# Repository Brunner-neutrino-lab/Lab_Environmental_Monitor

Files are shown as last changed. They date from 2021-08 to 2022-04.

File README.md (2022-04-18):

# Project Description
The goal of this device is to be able to monitor air quality throughout the day with little maintenance, once the apparatus is fully set up. Everything depends on the Raspberry Pi, a microcontroller that can run programs and connect itself to various sensors. The sensors will measure the temperature, humidity, pressure, and dust levels. The Pi will take readings periodically, which will then be stored locally in the `Environmental_Data.csv` file. The key files of the project are: 
- `config.py` --> It allows the user to modify parameters such as reading and upload intervals, and sensor toggling .
- `Sensors_Functions.py` --> This file contains the functions needed to obtain readings from the sensors.
- `MAIN_PROGRAM.py` --> This file will take periodic readings of the surrounding environment 

# Weather Station Device Setup Guide 

This guide is here to help you connect and set up the different sensors to the Raspberry Pi. Everything works with the default `Raspbian OS`. If one needs help installing it onto the microSD card, visit [**this site**](https://projects.raspberrypi.org/en/projects/raspberry-pi-setting-up/2). If one wants to update their version, visit [**this site**](https://www.raspberrypi.org/documentation/raspbian/updating.md).

Once the OS is set up, and a keyboard and mouse are plugged in, please wire up the sensors as illustrated in the [**diagram**](https://github.com/Brunner-neutrino-lab/Lab_Environmental_Monitor/blob/main/DOCS/Photos/Wiring_Diagram.png). There are writen instructions [**here**](https://github.com/Brunner-neutrino-lab/Lab_Environmental_Monitor/blob/main/DOCS/WiringDiagram.md) if ever you need more details concerning the wiring.

If you are connecting an individual sensor without the use of `i2c`, you may skip over the next section, otherwise enabling the i2c interface is crucial for the sensor connection. The main program connects with all the sensors via the i2c interface. It allows for a more centralized and simple wiring scheme without using too many pins.

## Enabling the I2C interface

For a more detailed guide with photos, go [**here**](https://www.raspberrypi-spy.co.uk/2014/11/enabling-the-i2c-interface-on-the-raspberry-pi/).

Otherwise start by typing `sudo raspi-config` into the **Command line**

It will launch the raspi-config utility. From there:
- select **Interfacing Options** :
- Highlight the “I2C” option and activate: **Select**
- Select and activate: **Yes**
- If prompted to reboot highlight and activate: **Yes**

Once the i2c interface is set up and the devices are wired up, run the following command in the terminal: `sudo i2cdetect -y 1`. It will give you all the hexadecimal addresses for the devices which should be double-checked with the ones in the `config.py`. If the values do not match, modify them in the code so it matches the one from the terminal. You will only need to activate the i2c interface once and then you will not have to worry about it anymore.

## Software Setup

The first thing to do is to download the missing packages by entering the following commands in the terminal.

```
sudo apt install python3-pip
sudo apt install libatlas3-base
sudo pip3 install RPi.bme280
```

## How to run

Make sure everything is properly set up and that all the criteria below are met:
- i2c is enabled on the Raspberry Pi.
- The sensors are wired accordingly to the wiring [**diagram**](http://132.206.126.37/bvllab/particulate-sensor/blob/master/DOCS/Photos/Wiring_Diagram.png).
- The addresses from `i2cdetect -y 1` match the ones found in the `config.py` file.

Navigate through the directories until you are in the Main Folder. From there, run `nohup sudo python3 MAIN_PROGRAM.py &`. The nohup allows it to run even when the terminal is closed and the `&` symbol allows it to run as a background app. 

----------------

## Adding Additional Sensors

To add additional sensors, ideally they should be connected using the i2c module, making the wiring much easier and straight forward. The code to run the sensor should be in python, since most of the code is written in that language. 

- To start off, create a new variable in the `config.py` file to toggle the sensor on or off. It should be called something like NewSensor**Status** and will take values of either `1` or `0`. Then, in `Sensors_Functions.py` create the new variable: `NewSensor=config.NewSensorStatus`
- Once a systematic method of obtaining readings from the sensor is achieved, simply add a new function in the `Sensors_Functions.py` program before the `header()` function towards the end. The newly-created function should only return the observed reading such as temperature or pressure. No need for timestamps since the `Header()` function takes care of that. 
- In the `Header()` function, add a new "if" statement going along the lines of:
```
if NewSensorStatus==1:
    statement += ',NewSensor_units_used'
```
- Finally, in the `data()` function, add a new "if" statement looking like this:
```
if NewSensorStatus==1:
    statement += ',' + str(NewSensor())
```

## Contributors
- Felix Belair
- Chris Chambers
- Soud Al Kharusi

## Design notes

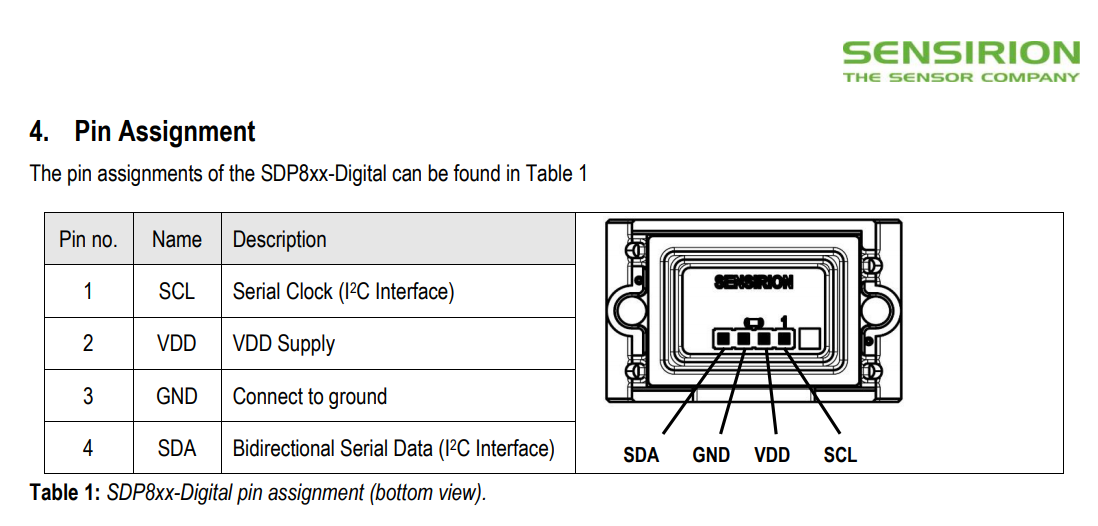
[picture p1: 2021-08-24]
DOCS/Photos/SDP810.png

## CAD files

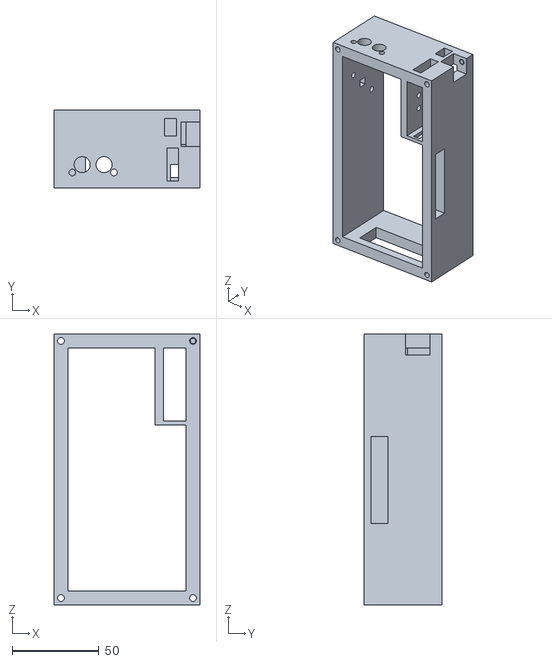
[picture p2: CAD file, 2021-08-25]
DOCS/3D Printing Files/LWS001_CaseBody.STL
84.0 x 45.0 x 156.0

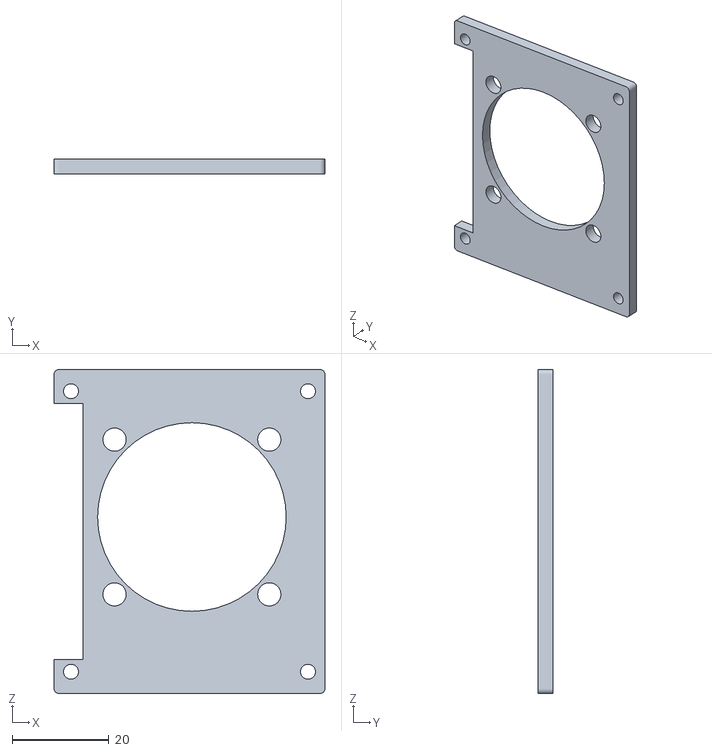
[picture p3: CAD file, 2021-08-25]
DOCS/3D Printing Files/LWS001_Fan_Bracket.STL
56.0 x 3.00 x 67.0

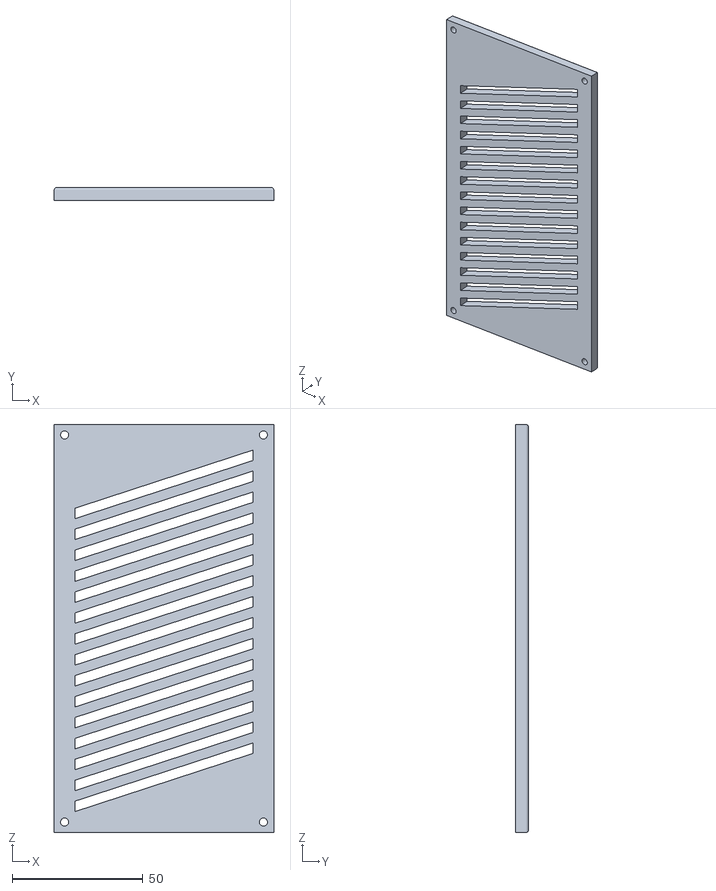
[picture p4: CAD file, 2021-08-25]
DOCS/3D Printing Files/LWS001_CaseLid.STL
84.0 x 5.00 x 156.0

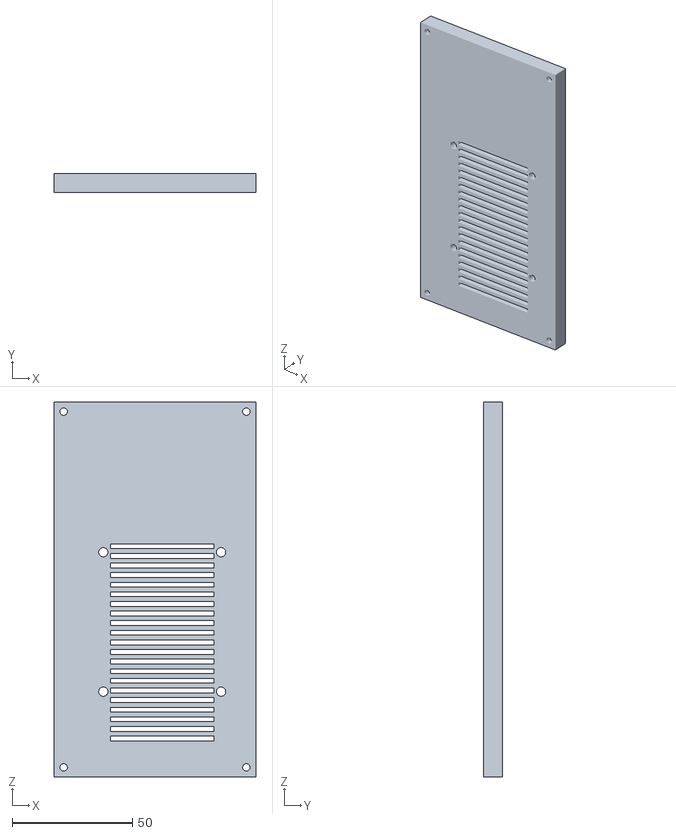
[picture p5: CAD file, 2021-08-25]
DOCS/3D Printing Files/LWS004_CaseBottom.STL
84.0 x 8.00 x 156.0

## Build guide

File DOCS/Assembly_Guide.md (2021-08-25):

# Brief Overview 

The goal of the project is to record environmental variables continuously over years with the use of various sensors such as a particulate counter or pressure differential sensor, to then upload the data to a server using a Raspberry Pi. Using various python submodules specific to each sensor, properties such as temperature, pressure differential, humidity, and dust levels are monitored and uploaded to a database at periodic time intervals. This would allow the user to verify whether the lab has a positive pressure differential relative to the outside to keep the dust out and to correlate when and how the dust particles enter. A 3d-printed case has been designed to package all these components together.

# Parts Needed 

* [Raspberry Pi 4](https://www.raspberrypi.org/products/raspberry-pi-4-model-b/) (The mastermind behind the project)
* [SPS30](https://www.sensirion.com/en/environmental-sensors/particulate-matter-sensors-pm25/) (Dust sensor)
* [SDP810](https://www.sensirion.com/en/flow-sensors/differential-pressure-sensors/sdp800-proven-and-improved/) (Pressure Differential sensor)
* [BME280](https://www.sparkfun.com/products/15440) (Atmospheric sensor that measures the Temperature, Humidity and Pressure)
* [Fan](https://www.sparkfun.com/products/15504) (will be placed above the Pi for it to cool off efficiently)
* [Small Soldering Board](http://www.proto-advantage.com/store/product_info.php?products_id=200062) (compact way to wire everything)
* 4x M2.5x6mm Standoffs (Raises the Pi slightly off the ground)--Must use this dimension since the openings for the Pi rely on the 6mm standoffs. McMaster-CARR number part:98952A103 
* 4x M2.5x12mm Standoffs (Raises the fan above the Pi)--Other heights may be used such as 14mm or 16mm if you do not have 12mm standoffs. McMaster-CARR number part:98952A109 
* 19x M2.5 Threaded Inserts (Allows us to use screws) McMaster-CARR number part:94180A321
* 10x M2.5x8mm Screws (used to attach fan onto the bracket, the lid, and SPS30) McMaster-CARR number part:91292A012
* 7x M2.5x10mm Screws (used to attach the BME280 and bottom part of the case) McMaster-CARR number part:91292A014
* 2x M2.5x16mm Screws (used to attach the SDP810) McMaster-CARR number part:91292A018
* 4x M4x16mm Screws (used for the fan) McMaster-CARR number part:90751A119
* 4x M4 nuts (also used for the fan) McMaster-CARR number part:91415A020
* Header pins (male and female)
* Jumper wires

# Software 
Here is a breif description of each program
* **The config.py** file can be modified by the user if ever they want to change something such as the time interval between scans or the I2C addresses for the sensors.
* **The MAIN_PROGRAM.py** does the data collection and the data upload.
* **The Sensors_Functions.py** is responsible for obtaining readings for all the sensors and for formatting the data. A python function is created for each sensor, and when called, returns a reading from that particular sensor. 

## Data File Format
The data being acquired is stored with headers....

* **timestamp:** This is the time at which the data was taken. The format is YYYY-MM-DD hh:mm:ss.
* **Temperature_C:** This is the temperature of the lab measured in Celsius. The readings should be around 21 degrees or so.
* **Pressure_Torr:** This is the pressure of the lab in Torr. Typically, the readings should be near 760Torr, which is the equivalent of 1 atmosphere.
* **Percent_Humidity:** This is the relative humidity in the air. At a given temperature, air can hold a certain amount of water vapor. Here it gives the ratio between the measured amount of water vapor present to the max carrying capacity at a given temperature.
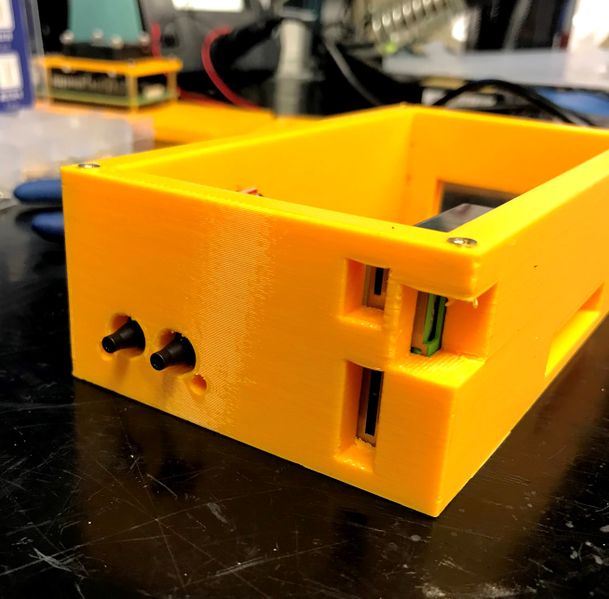
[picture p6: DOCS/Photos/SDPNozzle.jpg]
* **Differential_Pressure_Pa:** This is the difference in pressure between the 2 nobs on the SDP810, measured in Pascale. Once the SDP810 is placed inside the case, it will measure the pressure from the nozzle on right minus the pressure of the nozzle on the left, when viewed from this angle: 

It can give out both positive and negative values for the pressure difference, depending on which nozzle reads a higher pressure. This information comes from a diagram from this [data sheet](https://www.sensirion.com/fileadmin/user_upload/customers/sensirion/Dokumente/8_Differential_Pressure/Datasheets/Sensirion_Differential_Pressure_Datasheet_SDP8xx_Digital.pdf). 
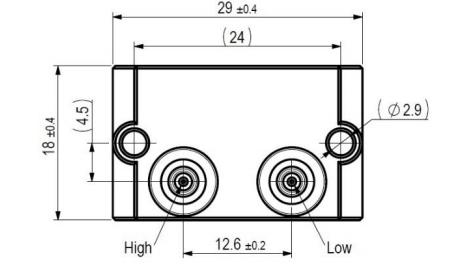
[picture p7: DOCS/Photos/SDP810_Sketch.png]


The sensor will return the difference between the High pressure nozzle to the Low pressure one in the diagram.

* **MC1um_ug_per_m3:** This measures the mass concentration of particles between 0.3um to 1um for a given volume of 1 meter cube in ug. In other words, take 1 meter cube of air and weigh all the particles between 0.3um and 1um and the total mass is the returned final reading (in ug). 
* **MC2point5um_ug_per_m3:** This measures the mass concentration of particles between 0.3um to 2.5um for a given volume of 1 meter cube in ug. In other words, take 1 meter cube of air and weigh all the particles between 0.3um and 2.5um and the total mass is the returned final reading (in ug). 
* **MC4um_ug_per_m3:** This measures the mass concentration of particles between 0.3um to 4um for a given volume of 1 meter cube in ug. In other words, take 1 meter cube of air and weigh all the particles between 0.3um and 4um and the total mass the final reading. 
* **MC10um_ug_per_m3:** This measures the mass concentration of particles between 0.3um to 10um for a given volume of 1 meter cube in ug. In other words, take 1 meter cube of air and weigh all the particles between 0.3um and 10um and the total mass is the returned final reading (in ug).
* **0point5um_Counts_Per_cm3:** This measures the number of particle counts between 0.3um to 0.5um for a given volume of 1 centimeter cube. In other words, take 1 centimeter cube of air and count all the particles between 0.3um and 0.5um and return the number of counts.
* **1um_Counts_Per_cm3:** This measures the number of particle counts between 0.3um to 1um for a given volume of 1 centimeter cube. In other words, take 1 centimeter cube of air and count all the particles between 0.3um and 1um and return the number of counts.
* **2point5um_Counts_Per_cm3:** This measures the number of particle counts between 0.3um to 2.5um for a given volume of 1 centimeter cube. In other words, take 1 centimeter cube of air and count all the particles between 0.3um and 2.5um and return the number of counts.
* **4um_Counts_Per_cm3:** This measures the number of particle counts between 0.3um to 4um for a given volume of 1 centimeter cube. In other words, take 1 centimeter cube of air and count all the particles between 0.3um and 4um and return the number of counts.
* **10um_Counts_Per_cm3:** This measures the number of particle counts between 0.3um to 10um for a given volume of 1 centimeter cube. In other words, take 1 centimeter cube of air and count all the particles between 0.3um and 10um and return the number of counts.
* **Typical_Particle_Size_um:** The typical particle size (TPS) gives an indication on the average particle diameter in the sample aerosol in um. Such output correlates with the weighted average of the number concentration bins measured with a TSI 3330 optical particle sizer. Consequently, lighter aerosols will have smaller TPS values than heavier aerosols.

# Physical Design 
Once all the components have been acquired (Raspberry Pi and sensors), a case has been designed to package everything together. The case is 3d printed and the **SolidWorks** design files can be found on [thingiverse](https://www.thingiverse.com/). At the moment, we are using the **Top_Fan_configuration** design, where the fan lies above the Raspberry Pi to cool it off. In that folder, the **3D print** folder contains all the parts that have to be printed (lid, main body, fan bracket, bottom case).

## Assembly Instructions (Top Fan Configuration)

To start, make sure you have all the material listed above and that the case components have been printed. 

### Fan and Bracket

* With the use of the **M4 nuts** and **M4x16mm screws**, clamp the fan onto the bracket. Ideally, the fan should be oriented such that the air should flow from below the bracket through the fan. This would ensure that the hot air is leaving the chip and going out of the case.
Here are 2 photos showing how it should look like once attached. 

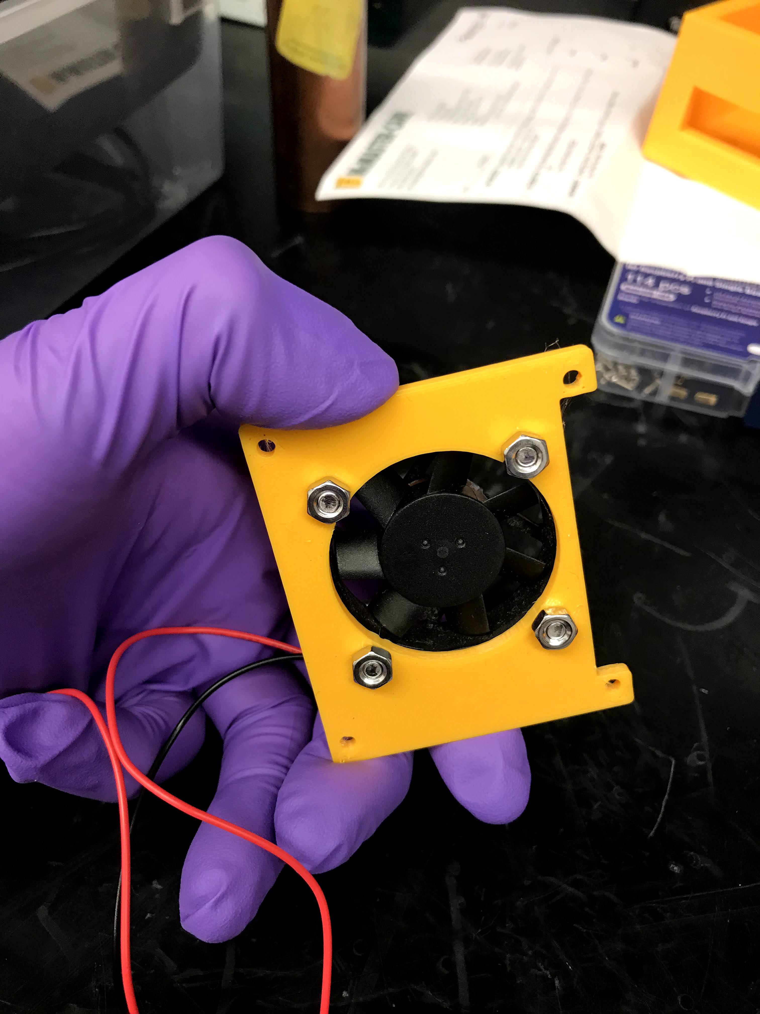
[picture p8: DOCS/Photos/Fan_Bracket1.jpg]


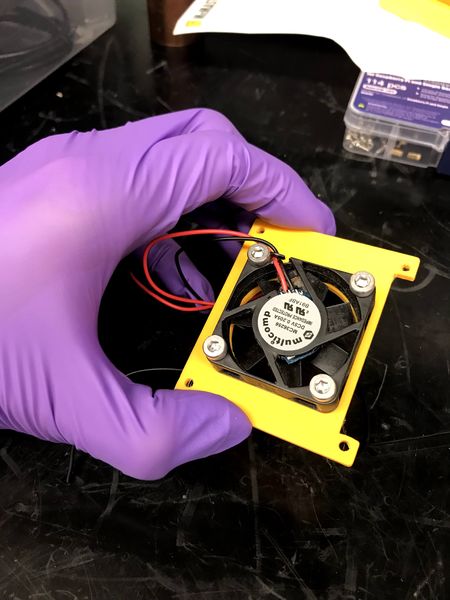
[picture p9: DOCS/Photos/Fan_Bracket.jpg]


Once this component is assembled, put it aside and we will use it in a few steps.

### Case Bottom

* Heat up and place the '''M2.5 threaded inserts''' into the 4 prearranged holes near the vent slits. They will be used to mount the Raspberry Pi.
* Once placed, screw in the '''M2.5x6mm Standoffs'''.

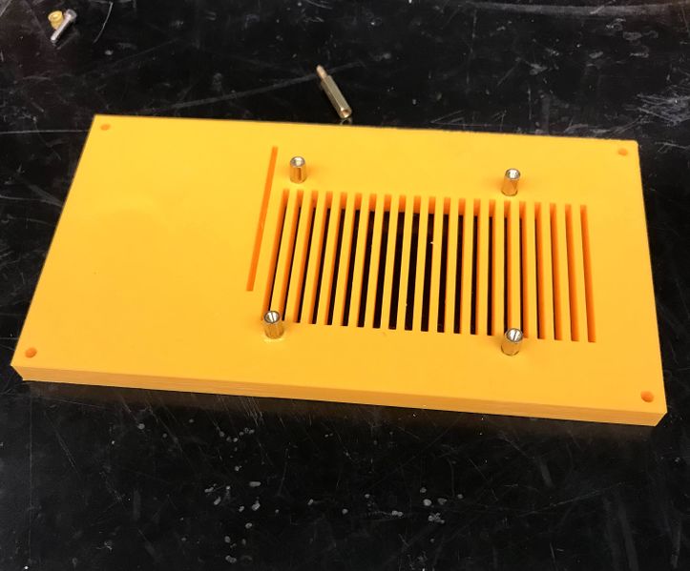
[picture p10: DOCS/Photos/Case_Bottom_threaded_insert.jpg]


* We can then proceed to mount the '''Raspberry Pi''' onto the corresponding standoffs by securing it with '''M2.5x12mm Standoffs'''. Make sure that the side with the USB and Ethernet ports is near the edge of the case and not the other way around. The 12mm standoffs will be used to place the fan above the Pi.

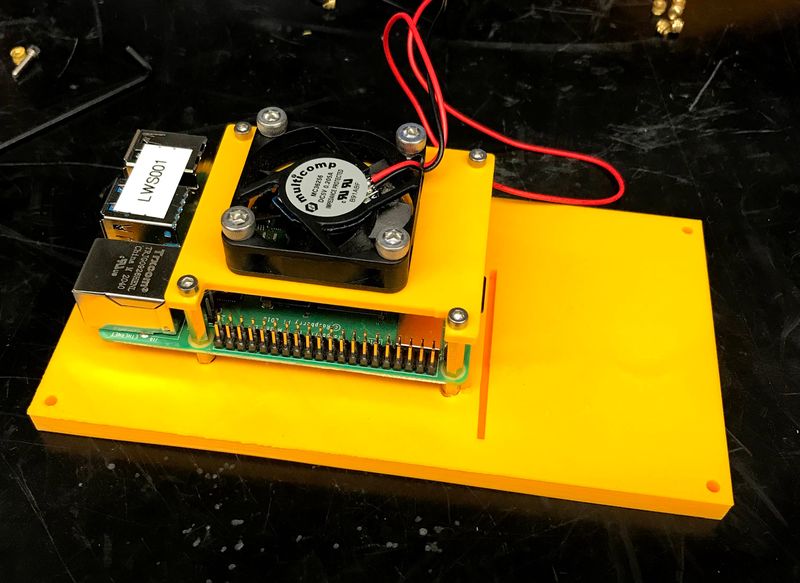
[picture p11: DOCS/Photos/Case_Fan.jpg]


* From there, we can take the Bracket-Fan component that we assembled in the first step, and mount it onto the standoffs using '''M2.5x8mm screws'''. For an optimal wiring experience, be sure to orient the bracket such that a hole is placed above the Raspberry Pi GPIO pins.

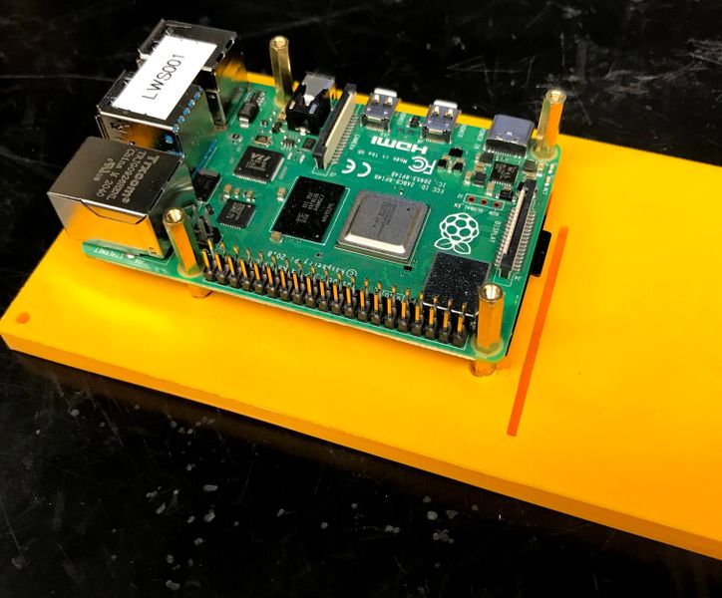
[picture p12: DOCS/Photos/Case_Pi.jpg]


### Main Body

* In the four outer corners of the main body of the case, heat up and place the '''M2.5 threaded inserts''' into the prearranged holes. Do this for the top and bottom holes of the corners.
* In all the inner holes of the case, heat up and place the '''M2.5 threaded inserts''' into the prearranged holes. This includes 2 for the SPS30, 3 for the BME280 and 2 for the SDP810.
* Place the '''SPS30''' in its assigned corner and fix it into place with 2 '''M2.5x8mm screws'''. Make sure the openings in the case align with the air intakes/outtakes of the sensor. 
* Place the '''SDP810''' by passing its 2 nozzles through the 2 wider holes. Make sure that it is oriented the right way up, such that its mounting holes align with the threaded inserts we placed earlier. Use 2 '''M2.5x16mm''' screws to secure it into place.
* The order of these steps is important since we cannot place the SDP810 once the BME280 is already placed. So once the SDP810 is mounted, we can now mount the '''BME280''' by inserting 3 '''M2.5x10mm screws'''. Make sure that the sensor component (the little box positioned in the middle) is facing outwards and aligned with the little opening.

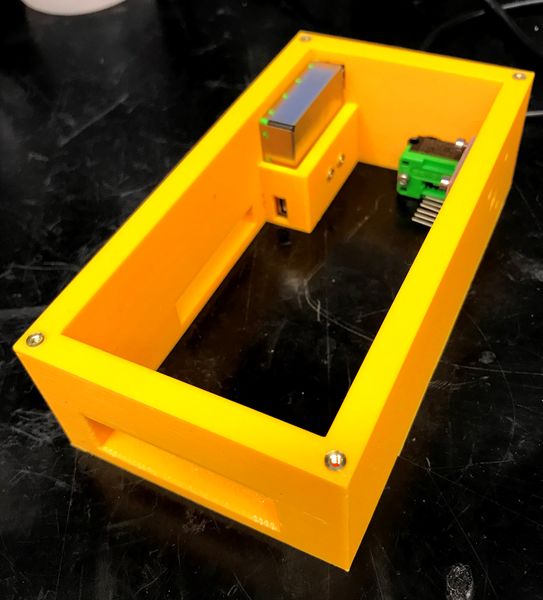
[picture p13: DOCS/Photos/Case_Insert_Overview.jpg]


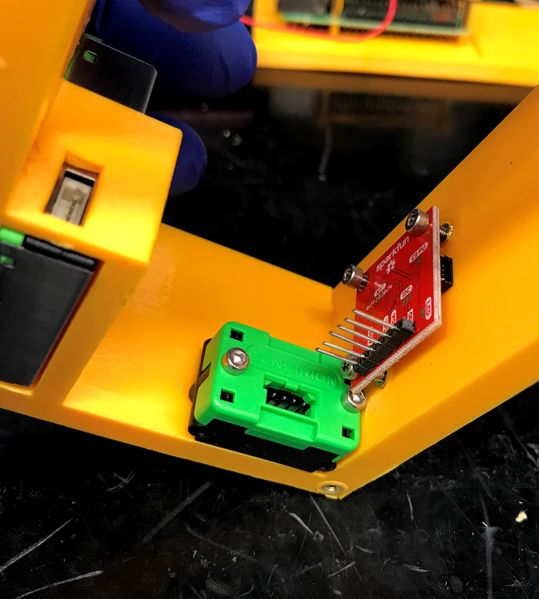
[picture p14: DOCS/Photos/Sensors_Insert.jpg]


### Soldering Board

* Using the small solder board, solder in a group of '''4 header pins''' for the RGB LED and a group of '''6 header pins''' for the rest of the sensors and the fan (the corresponding rows will be: 5V, 3.3V, SCL, SDA, Ground, Ground). The positioning is arbitrary, but in the photo, the header pins are placed in the upper row. These pins will be connected to the Pi with wires and the slots below them will connect to the various sensors. The use of the header pins allows us to rearrange a configuration without losing too much time. 

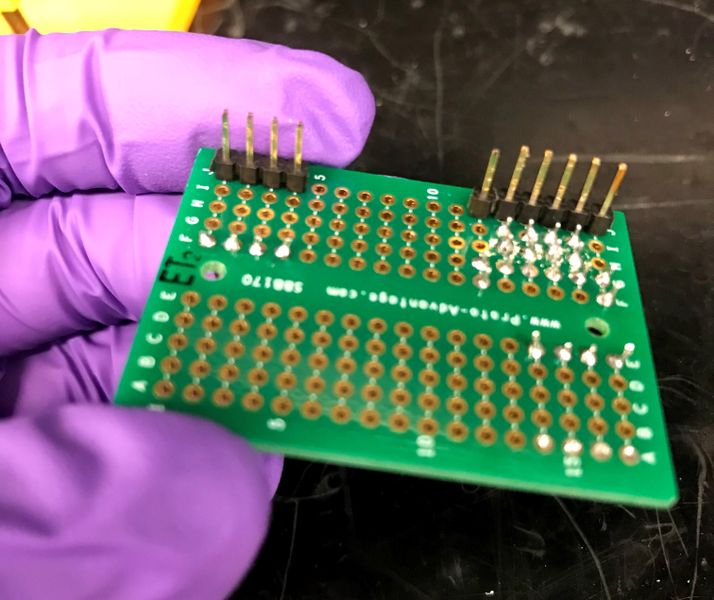
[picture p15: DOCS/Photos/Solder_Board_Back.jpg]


 In this photo, the 4 header pins for the RGB LED are placed on the far left, and the 6 others are placed on the right side of the board, all of which are on the top row.

* Flip the board over and solder in the '''RGB LED''' below the 4 header pins. Once the LED has been soldered, solder in '''female header pins''' in the same arrangement as the image below. 

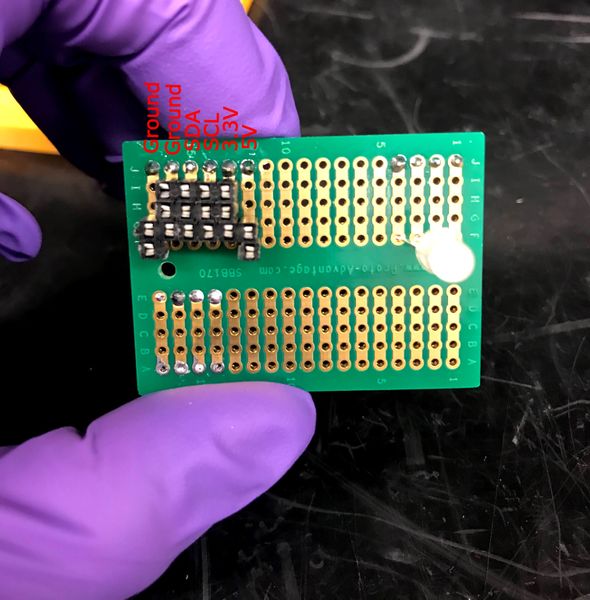
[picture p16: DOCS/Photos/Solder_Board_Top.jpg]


### Wiring

* After all the pins have been soldered, each sensor will connect their '''Ground, power source (3V or 5V), SDA, and SCL''' wires to their corresponding columns. The BME280 and SDP810 will use the first 2 rows (the order does not matter) since they both need the same 4 pins: 3V, SDA, SCL, and ground. The row with 6 pins is for the SPS30, as it will use everything except for the 3V pin (it is easier to solder in 6 consecutive pins, rather than having a hole in the middle). Finally, the fan will only use the 5V and the ground pin in the bottom row. If you take a closer look at the previous image (by clicking on it), you will see a column layout that has worked. From there, all the SDA pins will group up in the same column. The same is done for all the other pin types mentioned above (Ground, 3V, 5V, SDA, SCL). 

Wire layout for each sensors:
* If we look at the the '''SPS30''' (dust sensor) with the metal cap facing right and the wires pointing towards us, the top pin is #1 and the one in the bottom is #5. Then the pin roles are:
    * pin 1: 5V    (be careful to not connect it with the other 3.3V)
    * pin 2: SDA
    * pin 3: SCL
    * pin 4: Ground
    * pin 5: Ground (Very important to connect both grounds)

* If we look at the '''SDP810''' (pressure differential sensor) with the logo Sensirion facing upright. The pin on the very left will be pin 4 and the pin on the far right will be pin 1. 
    * Pin1 SCL
    * Pin2 3.3V
    * Pin3 Ground
    * Pin4 SDA

For the '''BME280''', the pins should be physically labeled, so no worries there. Do not worry if there are some unused pins on the BME280, since we only use 3V, Ground, SDA and SCL.

For the '''Raspberry Pi''', this photo should help out a bit.

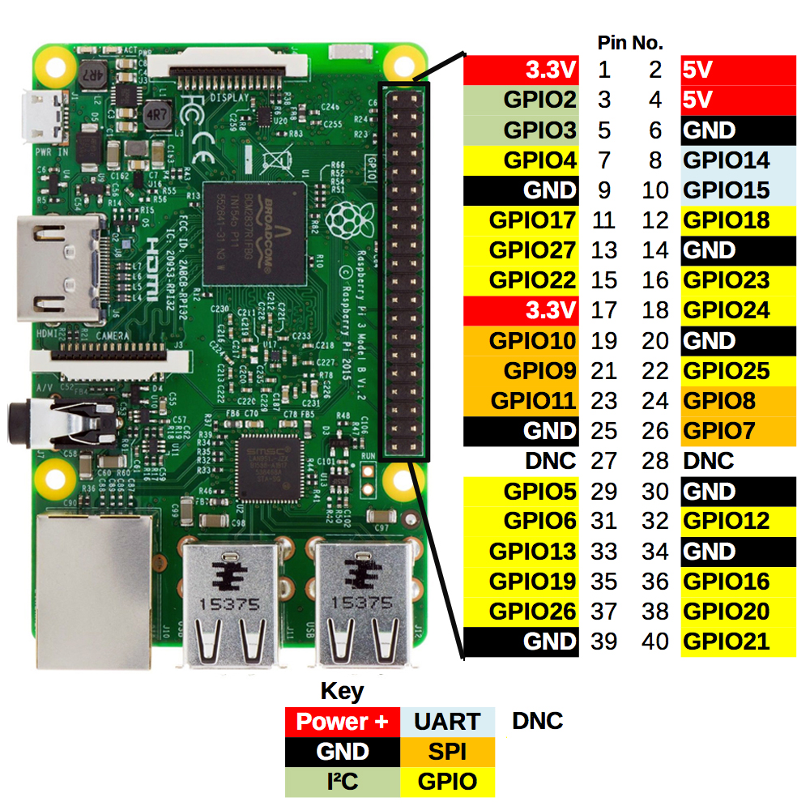
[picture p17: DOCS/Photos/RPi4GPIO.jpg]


*GPIO2 is for SDA and GPIO3 is for SCL.
*By default, the pins for the '''RGB LED''' are Red: GPIO13, Green: GPIO19, Blue: GPIO26. 

Here is a wiring diagram to help out. 



At first, it may look a little messy...

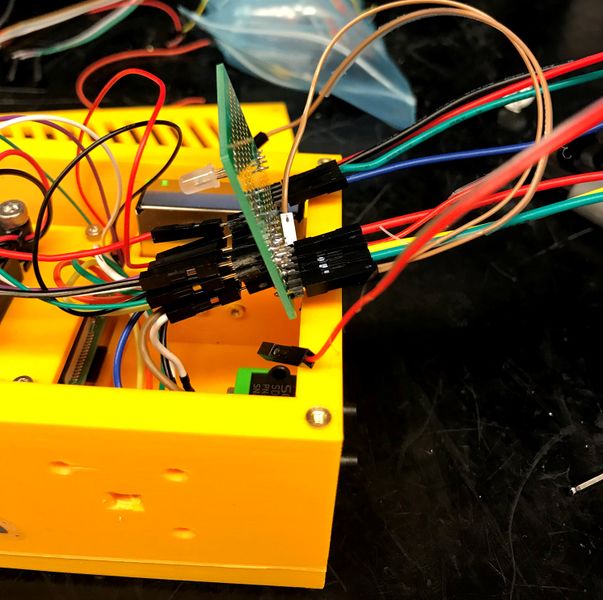
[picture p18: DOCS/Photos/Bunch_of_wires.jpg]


but once the Pi is wired up and we orient things a little better, things can place out to look like this:

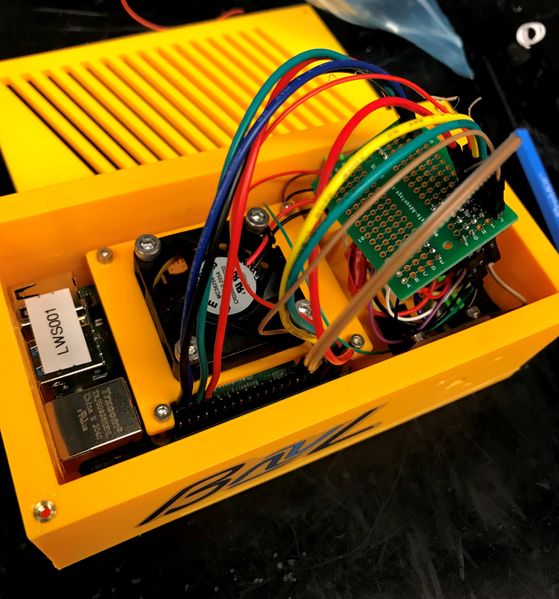
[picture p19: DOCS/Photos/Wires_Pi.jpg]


### Final Assembly

* Once things are wired up properly, flip the case over and mount the '''Case Bottom''' onto the Main Body with 4 '''M2.5x10mm''' screws. 
* Finally, flip the case over one last time to secure the '''Case Lid''' onto the Main Body with 4 '''M2.5x8mm''' screws.

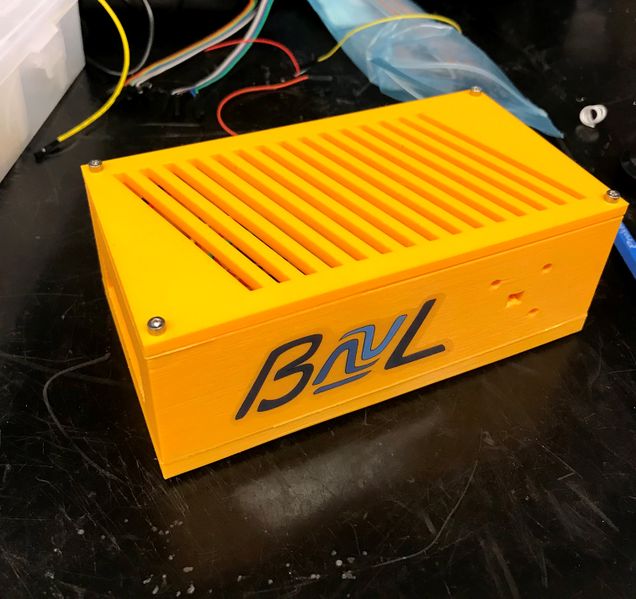
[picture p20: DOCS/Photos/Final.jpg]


# Known Issues

* If it is the first time running the program since it was last updated and errors are returned before it returns any readings, try rerunning the program once or twice.

* Another issue could be a wiring problem. Make sure all the components are wired properly. Take time to douche-check the wiring diagram to see if all the connections follow it. Make sure an electrical contact is properly made for all the sensors. It may be obvious if it is a jumper wire that is disconnected, but not so obvious if its the connector for the SPS30 or SDP810.

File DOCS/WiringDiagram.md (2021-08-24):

### Quick overview
For each sensor we will only need 4 connections: SDA, SCL, Voltage source, and ground. Even if there may be extra pins on the sensors, we will only need the 4 aforementioned pins. Since each sensor has a unique i2c address, all the SCL pins can be grouped up in the same column on a breadboard. The same should be done for the SDA pins. There are a few details concerning the power supply since the SPS30 uses 5V rather than 3.3V. Once all the wiring info is settled, you may wire up your sensors accoring to the [diagram](http://132.206.126.37/bvllab/particulate-sensor/blob/master/DOCS/Photos/Wiring_Diagram.png). To start off, we will first have to figure out which wires will do what.

### Pin labeling

For the **BME280**, the pins roles should be physically labeled on the sensor itself, so you shouldn't break a sweat for it. Soldering header pins is something I would recommend if it hasn't been done yet for that sensor. Do not worry if there are a few pins that will remain unused.

---------------------------------------------------------

If we look at the the **SPS30** (dust sensor) with the metal cap facing up, the pin on the left is pin 1 and the one on the right is pin 5. The pin roles are:

- pin 1: 5V    (be careful to not connect it with the other 3.3V)
- pin 2: SDA
- pin 3: SCL
- pin 4: Ground 
- pin 5: Ground (Very important to connect both grounds)

The reason why there are 2 ground wire connections, is because pin 4 determines how we connect the device. If it hangs there doing nothing, we select UART, and if we ground it, it chooses the i2c interface, which is what we are using. Furthermore, the ground pins cannot be connected with the ones from the other sensors since the voltage is different. For further guidance, here is a [diagram](http://132.206.126.37/bvllab/particulate-sensor/blob/master/DOCS/Photos/SPS30.png) of the sensor.

---------------------------------------------------------

If we look at the **SDP810** (pressure differential sensor) with the logo *Sensirion* facing upright. The pin on the very left will be **pin 4** and the pin on the far right will be **pin 1**. Please note that the order of the wires is different from the SPS30. For further guidance, here is a [diagram](http://132.206.126.37/bvllab/particulate-sensor/blob/master/DOCS/Photos/SDP810.png) of the sensor.

- Pin1 SCL
- Pin2 3.3V
- Pin3 Ground
- Pin4 SDA

---------------------------------------------------------
and finally for the Raspberry Pi we have:

- pin 1: 3.3V
- pin 2: 5V
- pin 3: GPIO2 ==>SDA
- pin 5: GPIO3 ==>SCL
- pin 6: GROUND (for the 5V dust sensor)
- pin 9: GROUND (for the 3.3V sensors)

This [diagram](http://132.206.126.37/bvllab/particulate-sensor/blob/master/DOCS/Photos/RPi4GPIO.jpg) shows the function of each pin on the Raspberry Pi 4.

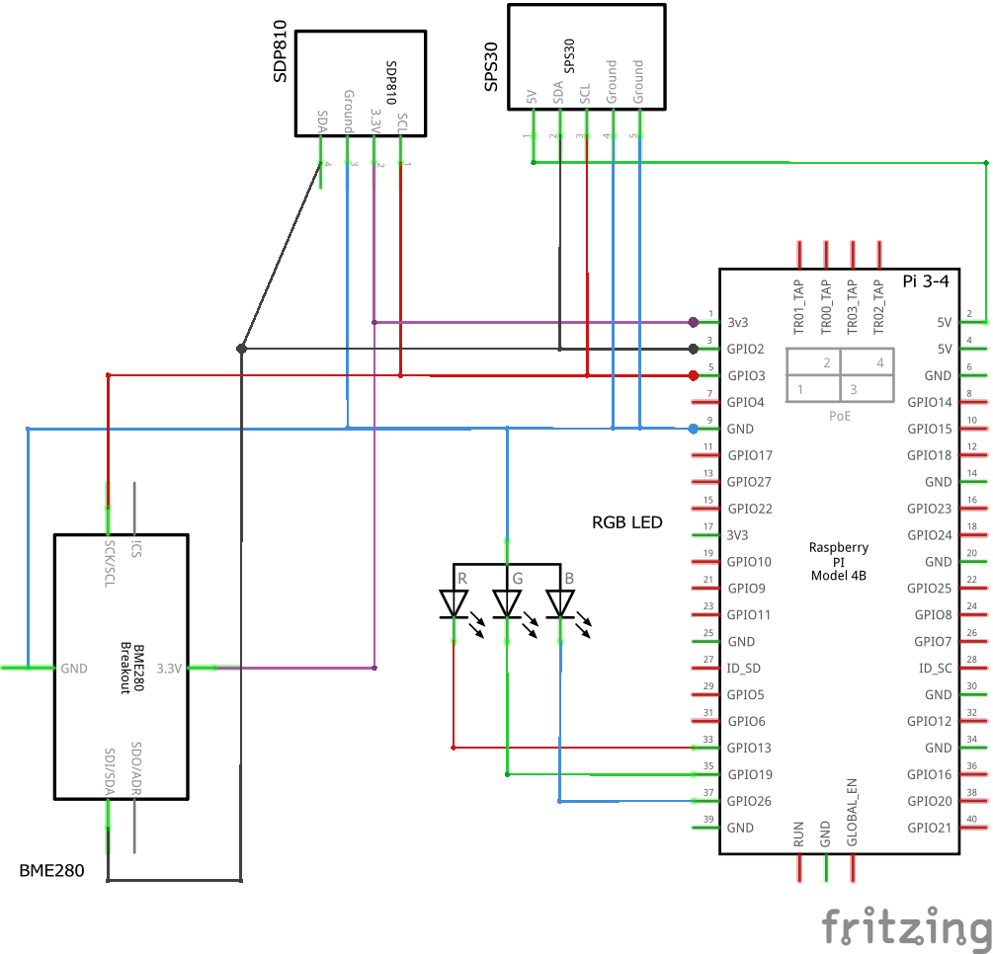
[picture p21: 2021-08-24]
DOCS/Photos/Wiring_Diagram.png

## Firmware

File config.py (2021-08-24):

#Sensor toggling: 
#1 turns it on and 0 turns it off
TemperatureStatus = 1
PressureStatus = 1
HumidityStatus = 1
Pressure_DiffStatus = 1   #SPD810
ParticulateStatus = 1     #SPS30
LightSignals = 1          #LED light to indicate when the system is running and when there are problems.

Interval_Between_Scans = 1 # in minutes 
csv_path = 'Environmental_Data.csv'  #Path to csv file

#These are the port addresses and have to be modified if the values do not match when <i2cdetect -y 1> is run
#The BME280 measures Temperature, Pressure and Humidity 
addressBME280 = 0x77 # Adafruit BME280 address, also known as the atmospheric sensor. Other BME280s may be different. To obtain it do <i2cdetect -y 1> in the terminal
addressDiff_Pressure = 0x25 #ths should be its i2c address but to verify it run <i2cdetect -y 1> in the terminal
addressSPS30 = 0x69 #for the sps30 dust sensor

#The GPIO pins which are attached to the RGB light
redGPIO = 13
greenGPIO = 19
blueGPIO = 26
